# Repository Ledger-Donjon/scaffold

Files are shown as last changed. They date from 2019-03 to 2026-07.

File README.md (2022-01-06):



# Scaffold

When performing hardware security evaluation of integrated circuits and embedded
platforms, the first step is to setup the device to be able to automate tests,
retrieve results and trigger instruments to perform measurements or inject
faults. Scaffold is an electronic motherboard designed to quickly setup,
instrument and test cirtcuits. The board can be controlled through USB using a
Python3 API, enabling easy development of tests. All the project is
Open-Hardware and Open-Source.

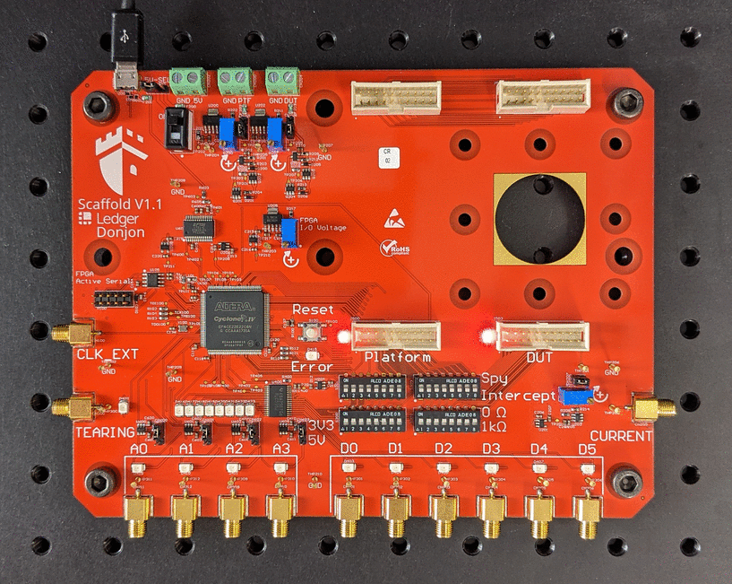
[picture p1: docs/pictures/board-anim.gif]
Scaffold board pictures


The FPGA architecture runs at 100 MHz and embeds many peripherals:

- 2 x UART,
- I2C (master),
- ISO7816 (master),
- SPI (master),
- Power supply controllers for each evaluation socket,
- 4 x Delay and pulse generators with 10 ns resolution
- 2 x chaining modules for advanced triggering
- Clock generator with glitching feature
- And more to come in the future!

The board also integrates an 11X analog amplifier with 200 MHz bandwidth for
power measurement. The on-board shunt resistor can be tuned from 0 to
100 Ohms.

Scaffold is able to operate from 1.5V to 3.3V devices: power supplies and I/O
bank voltage can be tuned thanks to adjustable voltage regulators. Scaffold can
be powered from USB or external power supplies.

Four special I/Os can generate 5V pulses, which are compatible with
*ALPhANOV PDM* laser sources (50 Ohm TTL).

## Getting the board

All the files required to fabricate the board are included in the repository.
If you do not wish to build it yourself, you can request for quotation by
sending a mail to scaffold@ledger.fr (only for Europe or USA shipping).

## Installation

Python3 library can be installed using pip:

    pip3 install donjon-scaffold

## Documentation

API documentation is available on [Read the Docs](https://donjonscaffold.readthedocs.io).

## Licensing

Scaffold is released under GNU Lesser General Public Licence version 3 (LGPLv3).
See COPYING and COPYING.LESSER for license details.

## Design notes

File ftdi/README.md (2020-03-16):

# FTDI EEPROM programming

Disconnect all USB-to-serial devices but the Scaffold board.

Install the package `ftdi_eeprom` and execute the `flash.sh` script as root to
program the EEPROM memory of the Scaffold FT232H device. This will configure
the vendor and description strings to respectively "Ledger" and "Scaffold".

Configuring the EEPROM is optional, but when programmed, the software is able
to recognize automatically which serial port corresponds to the Scaffold board.

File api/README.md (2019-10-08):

# scaffold board Python3 API

This is the Python3 API package for the Scaffold board.
See [Scaffold project on GitHub](https://github.com/Ledger-Donjon/scaffold).

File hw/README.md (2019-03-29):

## Authors

The hardware schematics and PCB have been designed by Julien Juan and
Guillaume Levant, at Ledger SAS.

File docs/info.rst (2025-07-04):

Product information
===================

Use and care
------------

Please handle your Scaffold board with care. The Scaffold board is not
waterproof. Make sure you use it indoor in a dry environment and keep away from
any liquids. This product is not a toy, make sure you keep it away from
children.

Changes or modifications to this product not expressly approved by Ledger could
void its compliance to test standards and negate the user's authority to operate
it.

If the product is used in a manner not specified by the manufacturer, the
protection provided by the equipment may be impaired.

Operating conditions
--------------------

For proper operation, the Scaffold board must be connected to a computer with
the USB2 cable. The product can be used with Linux, Windows and Mac. The board
API can be downloaded at https://github.com/Ledger-Donjon/scaffold.

+------------------------------------------+------------------------------------+
| USB supply voltage                       | 5 Vdc                              |
+------------------------------------------+------------------------------------+
| USB current rating                       | 1 A                                |
+------------------------------------------+------------------------------------+
| External supply voltage                  | 5 Vdc                              |
+------------------------------------------+------------------------------------+
| External supply current rating           | 1 A                                |
+------------------------------------------+------------------------------------+
| External platform supply maximum voltage | 5 Vdc                              |
+------------------------------------------+------------------------------------+
| External platform supply current rating  | 1 A                                |
+------------------------------------------+------------------------------------+
| External DUT supply maximum voltage      | 5 Vdc                              |
+------------------------------------------+------------------------------------+
| External DUT supply current rating       | 1 A                                |
+------------------------------------------+------------------------------------+
| For indoor use only                                                           |
+------------------------------------------+------------------------------------+
| Temperature range                        | 5°C to 40°C                        |
+------------------------------------------+------------------------------------+
| Maximum altitude                         | 2000 m                             |
+------------------------------------------+------------------------------------+
| Maximum relative humidity                | 80% up to 31°C,                    |
|                                          |                                    |
|                                          | Decreasing linearly to 50% at 40°C |
+------------------------------------------+------------------------------------+
| Expected pollution degree                | 2                                  |
+------------------------------------------+------------------------------------+

Three connectors allow using external power supplies instead of the 5 V USB
source. Power sources can be selected using the jumpers CN203, CN201 and CN206.
All the board can be powered using a single external power supply.
Independently, platform and DUT sockets can also be powered using external power
supplies.

External power supplies current must be limited to a current less than 5 A.
When using multiple power supplies, connect their ground signals together.

See :ref:`Using external power supplies <external_power_supplies>` for more information.

Manufacturer
------------

**Ledger**, 106 rue du Temple, 75003 Paris, France

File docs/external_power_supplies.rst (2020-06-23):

.. _external_power_supplies:

Using external power supplies
=============================

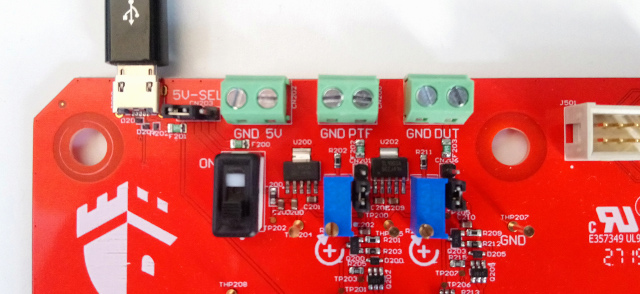
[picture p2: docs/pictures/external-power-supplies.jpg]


Three connectors allow using external power supplies instead of the 5 V USB
source.

- First green connector "GND 5V" allows connecting a 5 V - 1 A power source
  for powering all the board. The jumper "5V-SEL" on the left must be set to the
  right to disconnect the USB power source and connect the external power supply
  instead.

- Second green connector "GND PTF" allows connecting a 5 V - 1 A power source
  for powering the platform socket. The jumper below must be set to the top to
  disconnect the board power source and connect the external power supply
  instead.

- Third green connector "GND DUT" allows connecting a 5 V - 1 A power source
  for powering the Device Under Test platform socket. The jumper below must be
  set to the top to disconnect the board power source and connect the external
  power supply instead.

External power supplies current must be limited to a current less than 5 A.
When using multiple power supplies, connect their ground signals together.

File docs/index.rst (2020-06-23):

.. scaffold documentation master file, created by
   sphinx-quickstart on Fri Jul 13 13:31:07 2018.
   You can adapt this file completely to your liking, but it should at least
   contain the root `toctree` directive.

Welcome to scaffold's documentation!
====================================



.. toctree::
   :maxdepth: 2
   :caption: Contents:

   Getting started <getting_started.rst>
   Product information <info.rst>
   Platform and DUT sockets <sockets.rst>
   Using external power supplies <external_power_supplies.rst>
   Kits <kits.rst>
   Scaffold peripherals <peripherals.rst>
   Python API reference <api.rst>
   Architecture <architecture.rst>
   Building and flashing the FPGA bitstream <building_bitstream.rst>

Indices and tables
==================

* :ref:`genindex`
* :ref:`modindex`
* :ref:`search`

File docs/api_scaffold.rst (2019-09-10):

Main Scaffold API
=================

This page documents the main classes and methods of the Scaffold Python API.

Manipulating the attributes of the different modules of a :class:`Scaffold`
instance will read or write in the FPGA registers. Some registers may be cached
by the Python API, so reading them does not require any communication with the
board and thus can be fast.

.. automodule:: scaffold

.. autoclass:: Scaffold
    :members: __init__

.. autoclass:: Signal
    :special-members: __init__, __str__, __lshift__
    :members:

.. autoclass:: IO
    :members:

.. autoclass:: IOMode
    :members:
    :undoc-members:

.. autoclass:: Pull
    :members:
    :undoc-members:

.. autoclass:: UARTParity
    :members:
    :undoc-members:

.. autoclass:: UART
    :members:

.. autoclass:: ISO7816
    :members:

.. autoclass:: I2C
    :members:

.. autoclass:: SPI
    :members:

.. autoclass:: PulseGenerator
    :members:

.. autoclass:: Clock
    :members:

.. autoclass:: Chain
    :members:

.. autoclass:: LEDs
    :members:

.. autoclass:: Power
    :members:

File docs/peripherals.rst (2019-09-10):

Scaffold peripherals
====================

The FPGA system has many modules wrapping communication peripherals or utility
hardware. Each module exposes registers which can be read or written. Each
register has a unique address.

Every module has input and output signals. Thoose signals are illustrated in
each peripheral documentation like the following example:

.. modbox::
    :inputs: input_a, input_b
    :outputs: output_a, output_b, output_c*

Input and output signals can be routed to Scaffold I/Os. Some special output
signals have a feedback path and can be routed to other peripheral inputs.
Thoose are usually trigger signals and are represented with an extra arrow like
the signal `output_c` in the example above.

.. toctree::
  :caption: Contents:

   I/Os <ios.rst>
   UART <uart_module.rst>
   Power <power_module.rst>
   LEDs <leds_module.rst>
   ISO7816 <iso7816_module.rst>
   I2C <i2c_module.rst>
   SPI <spi_module.rst>
   Pulse generator <pulse_generator_module.rst>
   Clock generator <clock_module.rst>
   Chain triggers <chain_module.rst>
   Version <version_module.rst>

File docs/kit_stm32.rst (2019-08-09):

STM32F2 kits
============

STM32 kits allows communicating with the embedded ST bootloader of STM32F205 and
STM32F427 devices. It is possible to write the Flash memory to load code, and
then execute it after reset.

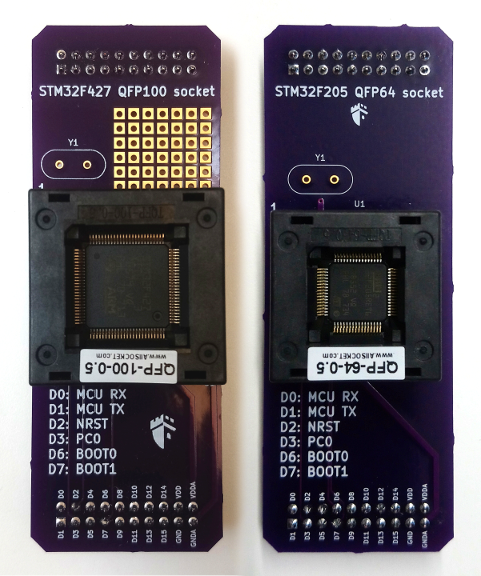
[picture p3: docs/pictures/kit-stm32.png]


Those QFP64 and QFP100 may suit other STM32 devices. Some breadboard space
allows customizing the daughterboard for special needs, such as clock or voltage
glitch electronics.

Python API example
------------------

The class :class:`scaffold.stm32.STM32` of the Python API provides methods to
communicate with the circuit and setup tests very quickly.

.. code-block:: python

    from scaffold import Scaffold
    from scaffold.stm32 import STM32

    stm = STM32(Scaffold('/dev/ttyUSB0'))
    # Load some code into Flash memory
    stm.startup_bootloader()
    stm.extended_erase()
    stm.write_memory(0x08000000, open('program.bin', 'rb').read())
    # Run the program
    stm.startup_flash()

Example script
--------------

An example file in `examples/stm32.py` can be used to load and execute code
onto a STM32F2 device.

.. code-block:: console

    $ python3 stm32.py -d /dev/ttyUSB0 --load program.bin --run
    Communication initiated
    Product ID: 0x0411
    Possible device match: stm32f2xxxx
    Get: 310001021121314463738292
    Bootloader version: 3.1
    Option bytes: ffaa0055ffaa0055ffff0000ffff0000
    RDP: no protection
    Erasing Flash memory...
    Programming...
    Verifying...
    Flash memory written successfully!
    Rebooting from Flash memory...

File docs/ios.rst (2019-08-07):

I/Os
====

The Scaffold Python API allows controlling and reading the I/Os of the board.
This can be useful, for instance, to control the reset signal of a device under
test. The following example shows how easy this can be done.

.. code-block:: python

    # Toggle D0 every second.
    for i in range(10):
        scaffold.d0 << 0
        time.sleep(1)
        scaffold.d0 << 1
        time.sleep(1)

    # Put D0 in high impedance state
    scaffold.d0 << None
    time.sleep(1)

    # Connect the output to the internal UART peripheral TX signal, and send a
    # message !
    scaffold.d0 << scaffold.uart0.tx
    scaffold.uart0.send('Hello world!')

It is also possible to read the current electrical state of an input of the
board:

.. code-block:: python

    if scaffold.d0.value == 1:
        print('Input is high!')

Finally, you can watch for events on an input. The event will be asserted if a 1
is detected. This works for short pulses (> 10 ns).

.. code-block:: python

    # Reset event flag
    scaffold.d0.event = 0
    # Wait some time
    time.sleep(1)
    # Lookup event register to know if a pulse has been received
    if scaffold.d0.event == 1:
        print('Event detected!')
        scaffold.d0.clear_event()

.. warning::
    I/Os internals have been refactored in 0.3. Registers are not the same as in
    0.2. Current API supports both 0.2 and 0.3 versions.

Programmable pull-resistors
---------------------------

Scaffold hardware version 1.1 comes with programmable pull resistors for D0, D1
and D2. This can replace pull-up resistors which were necessary for
bidirectionnal buses like the I/O signal of the ISO7816 interface. The pull
resistor can be configured using the Python API, as shown in the following
example:

.. code-block:: python

    scaffold.d0.pull = Pull.UP
    scaffold.d1.pull = Pull.DOWN
    scaffold.d2.pull = None  # Pull.NONE also accepted

Pull resistor value is 10 kOhm. When pull resistor is disabled, there is still
a weak pull-up resistor from the FPGA I/O itself.

Internal registers
------------------

+----+-------------------+
| a0 | 0xe000            |
+----+-------------------+
| a1 | 0xe010            |
+----+-------------------+
| a2 | 0xe020            |
+----+-------------------+
| a3 | 0xe030            |
+----+-------------------+
| dn | 0xe060 + 0x10 * n |
+----+-------------------+

+---------------+--------+-----+
| base + 0x0000 | value  | R/W |
+---------------+--------+-----+
| base + 0x0001 | config | W   |
+---------------+--------+-----+

value register
--------------

+---+---+---+---+---+---+-------+-------+
| 7 | 6 | 5 | 4 | 3 | 2 | 1     | 0     |
+---+---+---+---+---+---+-------+-------+
| *reserved*            | event | value |
+-----------------------+-------+-------+

value
  Reading this bit will return current logical state on the I/O.
  Setting this bit has no effect.
event
  This bit is set to 1 when the I/O logical state changes. It can be reset by
  writing 0 to it.

config register
---------------

+---+---+---+---+---+---+---+---+
| 7 | 6 | 5 | 4 | 3 | 2 | 1 | 0 |
+---+---+---+---+---+---+---+---+
| *reserved*    | pull  | mode  |
+---------------+-------+-------+

This register allows customizing the output mode of an I/O.

+------+----------------------------------------------------------------------+
| mode | Description                                                          |
+------+----------------------------------------------------------------------+
| 0    | **Auto**                                                             |
|      |                                                                      |
|      | The pin is driven by the routed peripheral.                          |
+------+----------------------------------------------------------------------+
| 1    | **Open-drain**                                                       |
|      |                                                                      |
|      | The pin is driven by the routed peripheral, but always acts as an    |
|      | open-collector.                                                      |
+------+----------------------------------------------------------------------+
| 2    | **Push-only**                                                        |
|      |                                                                      |
|      | The pin is driven by the routed peripheral, but is active only when  |
|      | a one is outputed.                                                   |
+------+----------------------------------------------------------------------+

If the I/O supports it, the pull resistor configuration can be configured. For
Scaffold hardware v1, no I/O supports this option. For Scaffold hardware v1.1,
the D0, D1 and D2 I/Os supports this option.

+------+--------------------+
| pull | Description        |
+------+--------------------+
| 0    | No pull resistor.  |
+------+--------------------+
| 1    | Pull-down resistor |
+------+--------------------+
| 2    | No pull resistor.  |
+------+--------------------+
| 3    | Pull-up resistor   |
+------+--------------------+

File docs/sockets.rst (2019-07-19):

Platform and DUT sockets
========================

The following figure is a simplified drawing for the Scaffold v1.1 socket
footprints. It can be used to design custom daughter-boards.

Female HE10 connectors can be used on the daughter-boards. All holes are aligned
on a 2.54 mm (100 mil) grid, which is compatible with most of the prototyping
breadboards for very cheap daughter-board making.



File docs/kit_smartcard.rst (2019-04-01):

Smartcard kit
=============

This kit allows communicating with any smartcard using 7816 protocol.

The class :class:`scaffold.iso7816.Smartcard` of the Python API provides
methods to communicate with an ISO7816 Smartcard and setup tests very quickly.
Currently, only T=0 protocol is supported by the API and it has not been tested
extensively yet.

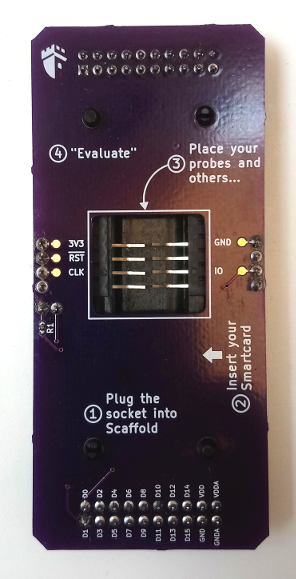
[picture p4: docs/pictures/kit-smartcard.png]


Pinout
------

+----+---------------------------------------------------------------------+
| D0 | I/O. This signal is pulled up with a resistor on the daughter board |
+----+---------------------------------------------------------------------+
| D1 | nRST                                                                |
+----+---------------------------------------------------------------------+
| D2 | CLK                                                                 |
+----+---------------------------------------------------------------------+
| D3 | Socket card presence contactor                                      |
+----+---------------------------------------------------------------------+

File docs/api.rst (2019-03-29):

Python API
==========
.. toctree::
  :caption: Contents:

  Scaffold <api_scaffold.rst>
  STM32 <api_stm32.rst>
  ISO7816 <api_iso7816.rst>

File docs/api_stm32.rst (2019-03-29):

STM32 API
=========

This API is for STM32 experimental daughter boards.

.. automodule:: scaffold.stm32

.. autoclass:: STM32
    :special-members: __init__
    :members:

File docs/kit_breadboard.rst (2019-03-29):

Breadboard kit
==============

The Scaffold breadboard provides solderable test points for all the DUT socket
pins. It can be used to mount a setup with any target.

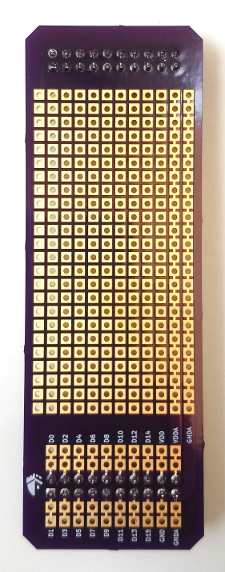
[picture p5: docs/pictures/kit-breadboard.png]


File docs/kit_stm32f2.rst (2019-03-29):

STM32F2 QFP64 kit
=================

This kit allows communicating with the embedded ST bootloader of STM32F2
devices. It is possible to write the Flash memory to load code, and then
execute it after reset.

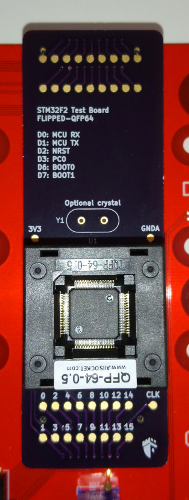
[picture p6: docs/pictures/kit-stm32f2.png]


The socket FLIPPED-QPF64 can be used to mount a STM32F2 device on its backside.
All pins of the package must be returned before inserting the device in the
socket. Pin 1 of the target device is as shown in the figure above. Make sure
the device is correctly inserted and all the needles of the socket touch their
corresponding PIN.

Python API example
------------------

The class :class:`scaffold.stm32.STM32` of the Python API provides methods to
communicate with the circuit and setup tests very quickly.

.. code-block:: python

    from scaffold import Scaffold
    from scaffold.stm32 import STM32

    stm = STM32(Scaffold('/dev/ttyUSB0'))
    # Load some code into Flash memory
    stm.startup_bootloader()
    stm.extended_erase()
    stm.write_memory(0x08000000, open('program.bin', 'rb').read())
    # Run the program
    stm.startup_flash()

Example script
--------------

An example file in `examples/stm32.py` can be used to load and execute code
onto a STM32F2 device.

.. code-block:: console

    $ python3 stm32.py -d /dev/ttyUSB0 --load program.bin --run
    Communication initiated
    Product ID: 0x0411
    Possible device match: stm32f2xxxx
    Get: 310001021121314463738292
    Bootloader version: 3.1
    Option bytes: ffaa0055ffaa0055ffff0000ffff0000
    RDP: no protection
    Erasing Flash memory...
    Programming...
    Verifying...
    Flash memory written successfully!
    Rebooting from Flash memory...

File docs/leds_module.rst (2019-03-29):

LEDs module
===========

The LEDs module allows controlling the LEDs of the board.

Python API example
------------------

.. code-block:: python

    # Adjust LEDs brightness
    # 0 is minimum
    # 1 is maximum
    scaffold.leds.brightness = 0.5

    # Toggle a LED every second
    scaffold.leds.d0.mode = LEDMode.VALUE
    for i in range(10):
        time.sleep(1)
        scaffold.d0 << 1
        time.sleep(1)
        scaffold.d0 << 0

    # Now flash the LED every second
    scaffold.leds.d0.mode = LEDMode.EVENT
    for i in range(10):
        time.sleep(1)
        scaffold.d0 << 1
        time.sleep(1)
        scaffold.d0 << 0

LEDs mode
---------

A/B/C/D LEDs can be lit according to two different modes:

- Event mode: the LED will flash when an rising or falling edge occurs on the
  monitored signal. This is the default mode. This mode allows seeing activity
  on the LED even when very short pulses happen.
- Value mode: the LED is ON when the monitored signal is high. When using this
  mode, a user may not be able to catch very short pulses. This mode is more
  appropriate for watching slow signals.

Registers
---------

+--------+------------+---+
| 0x0200 | control    | W |
+--------+------------+---+
| 0x0201 | brightness | W |
+--------+------------+---+
| 0x0202 | leds_0     | W |
+--------+------------+---+
| 0x0203 | leds_1     | W |
+--------+------------+---+
| 0x0204 | leds_2     | W |
+--------+------------+---+
| 0x0205 | mode       | W |
+--------+------------+---+

control register
^^^^^^^^^^^^^^^^

+---+---+---+---+---+---+----------+---------+
| 7 | 6 | 5 | 4 | 3 | 2 | 1        | 0       |
+---+---+---+---+---+---+----------+---------+
| *reserved*            | override | disable |
+-----------------------+----------+---------+

disable
  Write 1 to disable TLC5927 drivers output. Default is 0 (enabled).
override
  Sets the LEDs of the board to the values defined in led_n registers.

brightness registers
^^^^^^^^^^^^^^^^^^^^

+------------+---+---+---+---+---+---+---+
| 7          | 6 | 5 | 4 | 3 | 2 | 1 | 0 |
+------------+---+---+---+---+---+---+---+
| *reserved* | brightness                |
+------------+---------------------------+

brightness
  7-bits word which controls the brightness of the LEDs. See TLC5952 datasheet
  for more details.

leds_n registers
^^^^^^^^^^^^^^^^

*leds_n* registers define the state of the LEDs of the board when override bit
is set. Set a bit to 1 to turn the corresponding LED on, 0 to turn it off. Value
on reset is 0x00.

mode register
^^^^^^^^^^^^^

+----+----+----+----+----+----+----+----+----+----+----+----+----+----+----+----+----+----+---+---+---+---+---+---+
| 23 | 22 | 21 | 20 | 19 | 18 | 17 | 16 | 15 | 14 | 13 | 12 | 11 | 10 | 9  | 8  | 7  | 6  | 5 | 4 | 3 | 2 | 1 | 0 |
+----+----+----+----+----+----+----+----+----+----+----+----+----+----+----+----+----+----+---+---+---+---+---+---+
| *reserved*                  | d5 | d4 | d3 | d2 | d1 | d0 | c1 | c0 | b1 | b0 | a1 | a0 | *reserved*            |
+-----------------------------+----+----+----+----+----+----+----+----+----+----+----+----+-----------------------+

mode register is a 24-bit register. Write three times to update all the bits of
this register.

Each bit of this register sets the lighting mode of a LED. When bit is 0, the
corresponding LED will blink on a falling or rising edge of the monitored
signal. When the bit is 1, the LED will be lit as long as the monitored
signal is high. Default mode is 0 (event mode) for all LEDs.

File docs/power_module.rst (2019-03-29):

Power module
============

The power module controls two power supplies: the "platform" socket power
supply and the "dut" socket power supply. Each power supply can be turned
on and off. 

A positive input pulse on the "tearing" input of the board (SMA connector on
the left side) will automatically power-off both power supplies.

Python API example
------------------

.. code-block:: python

    # Turn DUT on
    scaffold.power.dut = 1 # True is also valid
    # Check current power supply status
    # (it may be off due to external tearing)
    if scaffold.power.dut: # Will return 0 or 1
        print('DUT is still ON')
    # Turn DUT off
    scaffold.power.dut = 0 # False is also valid

The following example controls both power supplies at the same time.

.. code-block:: python

    # Turn on all power supplies
    scaffold.power.all = 0b11 
    # Check current power status of both power supplies
    if (scaffold.power.all == 0b11):
        print('Both power supplies are ON')
    # Turn off all power supplies
    scaffold.power.all = 0b00

It is also possible to output the power enable signal to one of the IOs, for
triggering or monitoring:

.. code-block:: python

    scaffold.d0 << scaffold.power.dut_trigger

For more API documentation, see :class:`scaffold.Power`

Internal registers
------------------

+---------+--------+
| control | 0x0600 |
+---------+--------+

control register
^^^^^^^^^^^^^^^^

+---+---+---+---+---+---+----------+-----+
| 7 | 6 | 5 | 4 | 3 | 2 | 1        | 0   |
+---+---+---+---+---+---+----------+-----+
| *reserved*            | platform | dut |
+-----------------------+----------+-----+

dut
  Write 1 to enable the DUT socket power supply. Write 0 to disable. This bit
  is cleared when the tearing input is high.
platform
  Write 1 to enable the platform socket power supply. Write 0 to disable. This
  bit is cleared when the tearing input is high.

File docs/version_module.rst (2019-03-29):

Version module
==============

This module helps the software identifying the board. When
:class:`scaffold.Scaffold` connects to the board, the version string is
automatically queried and cached in the version attribute.

Python API example
------------------

.. code-block:: python

    # Read cached version string
    # Shall return something like 'scaffold-1.0'
    print(scaffold.version)

Internal registers
------------------

+--------+------+---+
| 0x0100 | data | R |
+--------+------+---+

data register
^^^^^^^^^^^^^

Reading multiple times this register will return the version string of the
board. A null character indicates the beginning (and end) of the version
string. Latest version string is "scaffold-1.0".

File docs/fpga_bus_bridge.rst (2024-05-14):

FPGA bus bridge
===============

The bus bridge allows reading and writing bytes on the internal FPGA bus using
commands sent in serial. This bridge is implemented in VHDL using a Finite State
Machine. The state machine manages the commands parsing and execution.

The state machine has a lot of states and is a bit complex. However, the parsing
and execution of a command is faster than the time required to receive an
incoming new command - making it hard to saturate the commands queue. The only
cases a command queue can be overflowed is when using polling commands - in such
cases the application may wait for the response before sending further commands.

Overflowing the commands queue will usually lead to entering the
error state as bytes will be discarded, resulting in data bytes being
interpreted as invalid command codes. When in error state, the error LED on the
board is lit. The only way to recover from the error state is pressing the reset
button.

State machine
*************

The following graph is the bus bridge finite state machine implemented in the
FPGA. This document is an help for understanding FPGA internals.

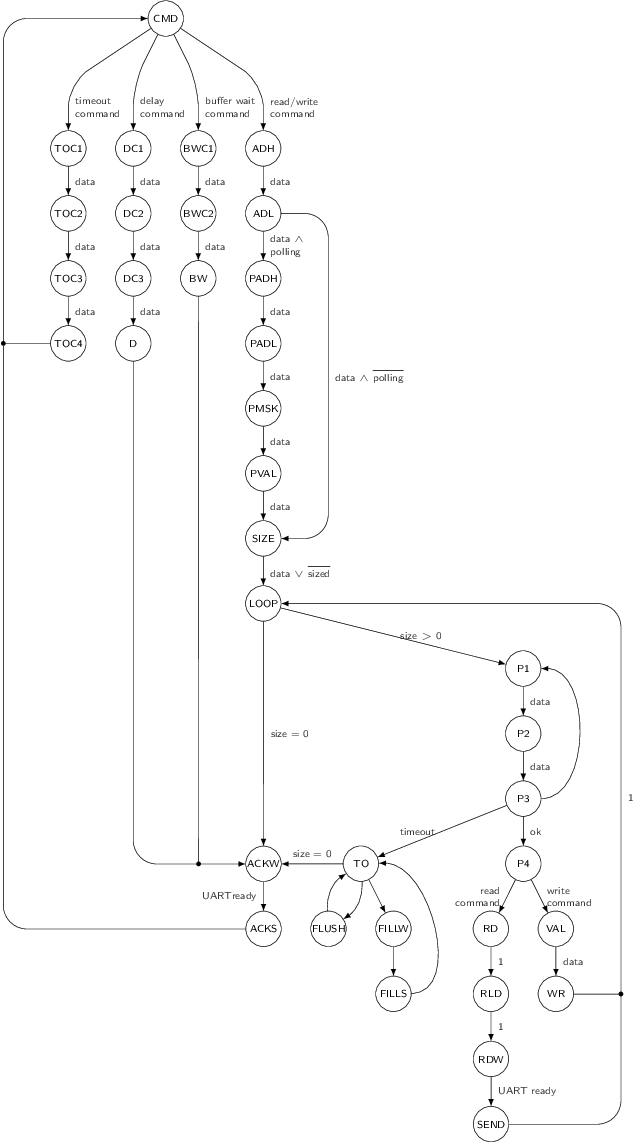
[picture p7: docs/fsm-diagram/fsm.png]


Details on states:

- ``CMD``: Idle state, awaiting for command byte.
- ``ADH``: Awaiting for read/write address high nibble.
- ``ADL``: Awaiting for read/write address low nibble.
- ``PADH``: Awaiting for polling address high nibble.
- ``PADL``: Awaiting for polling address low nibble.
- ``PMSK``: Awaiting for polling mask.
- ``PVAL``: Awaiting for polling value.
- ``SIZE``: Read/write size fetch. If the command does not require size
  parameter, use value 1 by default. Otherwise, wait and store next byte
  received on UART.
- ``LOOP``: Preload polling address on the bus for P1 and P2 states. Return to
  initial state if all bytes have been read or written.
- ``ACKW``: Wait for UART to be ready to transmit an acknoledge byte. This also
  acts as a delay cycle required for data bus to be available (due to
  pipelining).
- ``ACKS``: Send result byte on UART (command acknowledge or register value).
- ``P1``: First polling state. Assert bus read signal. Due to pipelining, the
  data read from the bus is available to the rest of the logic at ``P2``.
- ``P2``: Second polling state. Used for pipelining (registers the data read
  from the bus).
- ``P3``: Polling test. If polling value matches, leave polling by going to
  ``P4``. Otherwise, return to ``P1`` for a new polling read cycle.
- ``P4``: End of polling. Load register address on the bus.
- ``VAL``: Read from UART the byte to be written in register.
- ``WR``: Register write cycle.
- ``RD``: Register read cycle.
- ``RLD``: Register load cycle, waits for the read data to be available on the
  bus.
- ``RDW``: Wait for UART to be ready to transmit the read byte.
- ``RDS``: Send the read byte via UART.
- ``TO``: Timeout state. Loops until all unprocessed bytes have been discarded
  (write operation) or returned as zeros (read operation).
- ``FLUSH``: Cycle used to discard a byte from the input FIFO during a write
  operation which has timed out.
- ``FILLW``: Wait for UART to be ready.
- ``FILLS``: Transmit a filling byte to replace unread bytes.
- ``TOC1``: Awaiting for timeout configuration first byte.
- ``TOC2``: Awaiting for timeout configuration second byte.
- ``TOC3``: Awaiting for timeout configuration third byte.
- ``TOC4``: Awaiting for timeout configuration fourth byte.
- ``BWC1``: Awaiting for buffer wait configuration first byte.
- ``BWC2``: Awaiting for buffer wait configuration second byte.
- ``BW``: Awaiting for command buffer to be complete.
- ``DC1``: Awaiting for delay first byte.
- ``DC2``: Awaiting for delay second byte.
- ``DC3``: Awaiting for delay third byte.
- ``D``: Delay operation. Exits when the delay counter reaches 0.

Details on transition conditions:

- ``1``: Unconditionally pass to the next state at the next clock cycle.
- ``data``: True when the UART FIFO has a byte available.
- ``size``: Number of remaining bytes to be read or written.
- ``ready``: True when the UART of the bus bridge is ready to transmit a byte.
- ``read_command``: True when the fetched command byte corresponds to a bus read
  cycle command.
- ``write_command``: True when the fetched command byte corresponds to a bus
  write cycle command.
- ``buf_wait_command``: True when the fetched command byte corresponds to a bus
  buffer wait command.
- ``delay_command``: True when the fetched command byte corresponds to a bus
  delay command.

Polling timeout configuration
*****************************

A special command bit allows reconfiguring the polling timeout delay. The delay
parameter is stored in an internal 32 bits register and encodes a number of
clock cycles to wait during polling state (1 unit equals to 3 clock cycles).
When this register is set to 0, the timeout is disabled. Note that disabling
the timeout is not recommended since the FSM may stuck in a polling operation
forever or until general reset.

The maximum possible timeout duration is approximately 128 seconds.

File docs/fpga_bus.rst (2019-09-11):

FPGA bus
========

The internal global bus connects all the peripherals together. This bus is
controlled by the serial bridge which is connected to the host computer with
the USB link. The bus can perform only two simple operations:

- Read a byte from a register,
- Write a byte to a register.

The bus works using many signals:

- 16-bits address: bus_address,
- Write assertion signal: bus_write
- 8-bits write data: bus_write_data,
- Read assertion signal: bus_read
- 8-bits read data: bus_read_data

Using different data wires for read and write operations makes conflicts
between modules impossible. Also, some FPGA devices may not allow internal
bidirectional wires.

All the signals of the bus are synchronized to the system clock, on rising
edges.

Register read cycle
-------------------

.. wavedrom::

    { "signal": [
        {"name": "clock", "wave": "P...."},
        {"name": "bus_address", "wave": "x=x..", "data": ["address"]},
        {"name": "bus_read", "wave": "010.."},
        {"name": "bus_read_data", "wave": "x.=x.", "data": ["data"]},
        {"name": "bus_write", "wave": "0...."},
        {"name": "bus_write_data", "wave": "x...."}
        ],
      "config": { "hscale": 1.5, "vscale": 1.5 }
    }

|

Peripherals connected to the bus must present valid data one clock cycle after
the `bus_read` signal is asserted. This allow using FIFO blocks with
*read-ahead* option disabled, which is more performant.

Register write cycle
--------------------
    
.. wavedrom::    
    
    { "signal": [
        {"name": "clock", "wave": "P...."},
        {"name": "bus_address", "wave": "x=x..", "data": ["address"]},
        {"name": "bus_read", "wave": "0...."},
        {"name": "bus_read_data", "wave": "x...."},
        {"name": "bus_write", "wave": "010.."},
        {"name": "bus_write_data", "wave": "x=x..", "data": ["data"]}
        ],
      "config": { "hscale": 1.5, "vscale": 1.5 }
    }

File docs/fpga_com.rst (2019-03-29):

Communication protocol
======================

General architecture
--------------------

The FPGA has many embedded peripherals. Each peripheral has registers which can
be read/written to receive/send data and perform actions. Each register is
assigned a unique 16-bits address and is connected to the system data bus.

A bridge controller, inside the FPGA, controls the read and write operations on
the system data bus. This controller can be driven by a host computer using the
USB link, allowing the host computer to manipulate the registers connected to
the system data bus.

Protocol
--------

When connected to a host computer using a USB cable, the board is recognized as
a USB-to-Serial device from FTDI manufacturer. Baudrate is 2 Mbits/s, with one
stop bit and no parity check.

A very simple protocol is defined to perform read and write operations through
the serial device. To perform an operation, the following data must be sent to
Scaffold:

+----------------------+---------+----------------------+
| Command              | 1 byte  | Mandatory            |
+----------------------+---------+----------------------+
| Address              | 2 bytes | Mandatory            |
+----------------------+---------+----------------------+
| Polling address      | 2 bytes | When polling enabled |
+----------------------+---------+----------------------+
| Polling mask         | 1 byte  | When polling enabled |
+----------------------+---------+----------------------+
| Polling value        | 1 byte  | When polling enabled |
+----------------------+---------+----------------------+
| Size                 | 1 byte  | When size enabled    |
+----------------------+---------+----------------------+
| Data                 | N bytes | For write commands   |
+----------------------+---------+----------------------+

Bit 0 of command byte indicates if this is a read (0) or write (1) command.
Bit 1 indicates if size parameter is present (1 to enable size).
Bit 2 indicates if polling is requested for this command (1 to enable polling).
All other bits must be set to zero, otherwise the command is considered invalid
and Scaffold will enter error mode.

For write and read commands, a response is transmitted by the Scaffold board.
This response starts by the data bytes (for register read commands) and
terminates with a status byte. The status byte shall be equal to the size of the
processed data. If a command times out during polling, the returned status byte
will be lower than the size of the data.

Register polling
----------------

Read or write operations on registers can be conditioned to a given register
expected state. When polling is enabled, each read or write operation is
performed when the monitored register reaches a given value for some chosen
bits. Polling is enabled when bit 2 of command byte is 1. Read or write
operation is performed when ``(Register and Mask) = (Value and Mask)``.

Polling can be used for flow control when using a peripheral to process multiple
bytes. For instance, when using a SPI peripheral, polling can be used to wait
for incoming bytes.

The polled register can be different from the read or written register (two
different addresses can be passed in the command parameters: address and polling
address).

Polling timeout
---------------

Optionally, a timeout can be configured for polling operations. This is
particularly useful if receiving bytes from a peripheral is not guaranteed. When
the polling times out in a read operation, the remaining expected bytes are sent
by the board as zero. When the polling times out in a write operation, the
remaining bytes sent to the board are discarded by the bus bridge. The returned
acknowledge byte indicates the number of successfully processed bytes and will
be lower than the requested size in the command.

The timeout delay can be configured with a special command:

+----------------------+---------+----------------------+
| Command 0x08         | 1 byte  | Mandatory            |
+----------------------+---------+----------------------+
| Polling delay value  | 4 bytes | MSB first            |
+----------------------+---------+----------------------+

No response is expected after this command. The new delay value will be applied
for all the following commands. If the delay is set to zero, then the timeout is
disabled (which is the default).

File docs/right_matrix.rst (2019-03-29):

Output module
=============

The available I/Os of the scaffold board can be internally connected to any
module output. The "right matrix" controls which module output signals are
connected to which I/Os. Each I/O has a register storing its multiplexer
selecting the source signal.

Multiplexers selection table
----------------------------

+-------+-------------------------+
| Index | Signal name             |
+=======+=========================+
| 0     | z                       |
+-------+-------------------------+
| 1     | 0                       |
+-------+-------------------------+
| 2     | 1                       |
+-------+-------------------------+
| 3     | /power/dut_trigger      |
+-------+-------------------------+
| 4     | /power/platform_trigger |
+-------+-------------------------+
| 5     | /uart0/tx               |
+-------+-------------------------+
| 6     | /uart0/trigger          |
+-------+-------------------------+
| 7     | /uart1/tx               |
+-------+-------------------------+
| 8     | /uart1/trigger          |
+-------+-------------------------+
| 9     | /iso7816/io_out         |
+-------+-------------------------+
| 10    | /iso7816/clk            |
+-------+-------------------------+
| 11    | /iso7816/trigger        |
+-------+-------------------------+
| 12    | /pgen0/out              |
+-------+-------------------------+
| 13    | /pgen1/out              |
+-------+-------------------------+
| 14    | /pgen2/out              |
+-------+-------------------------+
| 15    | /pgen3/out              |
+-------+-------------------------+

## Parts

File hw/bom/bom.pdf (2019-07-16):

Quantity | Designator | Description | Manufacturer | Manufacturer PN | Manufacturer1 | Manufacturer1 PN | Manufacturer2 | Manufacturer2 PN
13 | C100, C101, C137, C200, C201, C202, C203, C204, C208, C209, C210, C217, C218 | Capacitor 0603 - 10uF - 16V - X5R - 20% | Murata | GRM188R61C106MA73D | TDK | C1608X5R1C106M080AB | Taiyo Yuden | EMK107BBJ106MA-T
51 | C102, C103, C104, C105, C106, C107, C108, C109, C110, C111, C112, C113, C114, C115, C116, C117, C118, C119, C120, C121, C122, C123, C124, C125, C126, C127, C128, C129, C130, C131, C132, C133, C134, C135, C136, C151, C153, C154, C205, C401, C600, C601, C602, C603, C605, C606, C607, C608, C609, C610, C611 Capacitor 0603 - 100nF - 16V - X7R - 10% | | Wurth | 885012206046 | Yageo | CC0603KRX7R7BB104 | Multicomp | MCCA000159
4 | C143, C144, C145, C146 | Capacitor 0603 - 10pF - 100V - COG - 5% | TDK | C1608C0G2A100D | Murata | GCM1885C2A100J | Samsung | CL10C100JC81PB
11 | C206, C207, C211, C212, C213, C214, C215, C216, C219, C220, C400 | Capacitor 0603 - 1uF - 16V - X7R - 10% | Kemet | C0603C105K4RACTU | Murata | GCM188R71C105K | Wurth | 885012206052
1 | C604 | Capacitor 0603 - 4.7uF - 16V - X5R - 10% | Murata | GRM188R61C475KE11 | TDK | C1608X5R1C475K080AC
13 | CN100, CN205, CN300, CN301, CN302, CN303, CN304, CN305, CN306, CN309, CN310, CN311, CN312 | Connector - SMA - Female - Horizontal - Mid Mount - Samtec - SMA–J–P–H–ST–EM3 | Samtec | SMA–J–P–H–ST–EM3
3 | CN200, CN202, CN204 | Connector - Wire to Board Terminal Block - 2-Positions - Wurth - 691213710002 | Wurth | 691213710002
7 | CN201, CN203, CN206, CN600, CN601, CN602, CN603 | Connector - Header - 3-Pin - single row - Male - Molex_90120-0123 | Molex | 90120-0123
1 | CN207 | Connector - Header - 2-Pin - single row - Male - Molex | Molex | 90120-0122
8 | D100, D101, D102, D103, D200, D201, D205, D206 | BAT60J | STMicroelectronics | BAT60J
3 | D202, D203, D204 | Diode - ESD -15kV -10GHz - ESDAXLC6-1BT2 | STMicroelectronics | ESDAXLC6-1BT2
2 | D400, D401 | Opto - DEL - RG 630/572nm 250/60 mcd - 20mA | Wurth | 150141RV73100
19 | D402, D403, D404, D405, D406, D407, D408, D409, D410, D411, D412, D416, D417, D418, D419, D420, D421, D422, D423 | Opto - DEL - Yellow 590nm - 2mA -30 mcd | Kingbright | AA3528LSYCKT/J3
1 | D415 | Opto - DEL - Red 625nm - 2mA -120 mcd | Kingbright | AA3528LSECKT/J3
4 | F200, F201, F202, F203 | Fuse 0805 - PTC Resettable - 1A - 0.5A - 6VDC - 0.9Ohms | Bel Fuse | 0ZCK0050FF2E | Bourns | MF-PSMF050X-2 | Littelfuse | 0805L050WR
1 | J200 | Connector - USB - Micro B - Wurth | Wurth | 629-105-150-521
4 | J500, J501, J502, J503 | Connector - Header - 20 Pins - Dual row - Shrouded - Male | Samtec | HTSS-110-01-G-D
3 | L100, L101, L200 | Ferrite - Bead - 0603 BLM18 | MURATA | BLM18KG101TN1D
1 | P100 | Connector - Header - 10 Pins - Dual row - Male | Samtec | TSW-105-07-G-D
2 | Q200, Q203 | Switch - PMOS 30V - STR2P3LLH6 - SOT23 | STMicroelectronics | STR2P3LLH6 | ON Semiconductor CPH3355-TL-W | | MCC | SI2307-TP
4 | Q201, Q202, Q204, Q205 | Switch - NMOS 30V - STT6N3LLH6 - SOT23-6 | STMicroelectronics | STT6N3LLH6
1 | R100 | Resistor 0603 - 47KOhm - 1/10W - 1% | YAGEO | RC0603FR-0747KL
20 | R101, R102, R103, R104, R105, R107, R108, R110, R111, R112, R301, R338, R339, R348, R349, R600, R601, R602, R604, R605 | Resistor 0603 - 10KOhm - 1/10W - 1% | Yageo | RC0603FR-0710KL | Panasonic | ERJ3EKF1002 | KOA Speer | RK73H1JHT..1002F
3 | R200, R207, R216 | Potentiometer - 50 kOhms - 10% - 0.5W - Bourns - 3296W-1-503RLF | Bourns Electronics | 3296W-1-503RLF
2 | R201, R209 | Resistor 0603 - 470Ohm - 1/10W - 1% | Yageo | RC0603FR-07470RP | Panasonic | ERJ3EKF4700 | KOA Speer | RK73H1JTTD4700F
2 | R202, R211 | Resistor 0603 - 15KOhm - 1/10W - 1% | Yageo | RC0603FR-1015KL | Panasonic | ERJ3EKF1502 | KOA Speer | RK73H1JHT..1502F
4 | R203, R204, R212, R213 | Resistor 0603 - 2Ohm - 1/10W - 1% | Vishay | CRCW06032R00FKEA
19 | R205, R214, R215, R304, R306, R308, R312, R316, R318, R320, R322, R326, R330, R332, R334, R340, R342, R346, R350 | Resistor 0603 - 1KOhm - 1/10W - 1% | Yageo | RC0603FR-071KL
1 | R206 | Resistor 0603 - 50Ohm - 1/10W - 1% | Vishay | CRCW060350R0FKEA
1 | R208 | Resistor 0603 - 100Ohm - 1/10W - 1% | Vishay | CRCW0603100RFKEA
1 | R210 | Potentiometer - 100 Ohms - 25 turns - 10% - 0.5W - Bourns - 3296W-1-101LF | Bourns Electronics | 3296W-1-101LF
1 | R217 | Resistor 0603 - 28KOhm - 1/10W - 1% | Yageo | AC0603FR-0728KL | Panasonic | ERJ3EKF2802 | KOA Speer | RK73H1JHT..2802F
11 | R300, R302, R303, R310, R311, R314, R315, R336, R337, R344, R345 | Resistor 0603 - 0Ohm - 1/10W - 1% | Vishay | CRCW06030000FKEA
2 | R400, R603 | Resistor 0603 - 4.75KOhm - 1/10W - 1% | Vishay | CRCW06034K75FKEA
1 | S100 | Misc - Button - WURTH 430152080826 | Wurth Elektronik | 430152080826
1 | S200 | Slide switch - 4A - 30VDC - APEM - 25136NAH | APEM | 25136NAH
4 | S300, S301, S302, S303 | Misc - DIP switch - 8 rows - TE connectivity - 1825057-7 | TE Connectivity | 1825057-7
22 | THP200, THP201, THP202, THP203, THP204, THP205, THP206, THP207, THP208, THP209, THP210, THP300, THP301, THP302, THP303, THP304, THP305, THP306, THP309, THP310, THP311, THP312 | Misc - Test pin - Through hole - Millmax - 6821-0-00-15-00-00-08-0 | Mill-max | 6821-0-00-15-00-00-08-0
1 | U100 | FPGA - 1.2V - Altera - EP4CE22E22C6 | Altera | EP4CE22E22C6
1 | U105 | IC - Serial configuration device - 16Mbits - SOIC8 - Altera - EPCS168N | Altera / Intel | EPCS16SI8N | Altera / Intel | EPCQ16ASI8N
3 | U200, U202, U205 | Power - LDO - Adj - 20V - 1.5A - SOT223-6 | Texas Instruments | TL1963ADCQR
3 | U201, U204, U208 | Power - LDO - 3.3V - 300 mA - SOT23-5L | STMicroelectronics | LDK130M33R
1 | U203 | Power - Operationnal amplifier - ADA4895-1 | Analog Device | ADA4895-1ARJZ-R
1 | U206 | Power - LDO - 1.2V - 300 mA - SOT23-5L | STMicroelectronics | LDK130M12R
1 | U207 | Power - LDO - 2.5V - 300 mA - SOT23-5L | STMicroelectronics | LDK130M25R
1 | U400 | Power - LED Driver - 24 LEDs - TLC5952 - HTSSOP32 | Texas Instruments | TLC5952DAP
4 | U600, U601, U602, U604 | Logic - Level Shifter - 1.65V - 5.5V - 420Mbps -3-state - SOT23-6 - Texas Instruments - SN74LVC1T45DBVR | Texas Instruments | SN74LVC1T45DBVR
1 | U603 | IC - USB-to-UART 1-CH 256Byte FIFO - 5V - 28-Pin SSOP | FTDI | FT232RL
1 | Y100 | Oscillator - 25MHz - 3.3V - HCMOS - ECS-2520S33-250-FN-TR | ECS | ECS-2520S33-250-FN-TR

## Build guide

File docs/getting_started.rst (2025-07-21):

Getting started
===============

Scaffold is a FPGA board made for security research on hardware embedded
devices. It is capable of communicating with many circuits using standard
protocols. It can be easily extended with new protocols by writing new
transceivers in VHDL or Verilog language, and integrating it in the proposed
scaffold global architecture. When exchanging messages with the devices under
tests, Scaffold can generate triggers for chosen commands, spy data on a bus or
intercept and traffic.

Scaffold board also embeds special electronics tailored for hardware attacks:

- Sense resistor and analog amplifier for real-time current measurement
- FPGA safety protections against voltage glitch attacks
- Controllable power switches
- Fast power tearing capability, for emergency shutdown of the device under test
- Delay and pulse generators, allowing firing glitches or laser pulses.

An easy-to-use python API is provided to control the board. https://github.com/Ledger-Donjon/scaffold

Board tour
----------



- **A**: USB2 link with host computer. Also used to power the board.
- **B**: Main board power switch.
- **C**: Switch the jumper to the right to power the board from an external 5 V
  power supply and not from the USB.
- **D**: External power supply for the platform socket.
- **E**: External power supply for the DUT socket.
- **F**: Adjustable voltage regulator for the platform socket. When the jumper
  is set on top position, this power source is not used and the platform socket
  is powered from the external power supply.
- **G**: Adjustable voltage regulator for the DUT socket. When the jumper is set
  on top position, this power source is not used and the DUT socket is powered
  from the external power supply.
- **H**: Adjustable voltage regulator for the I/O bank of the FPGA connected to
  the platform and DUT sockets. This allows setting the correct voltage
  depending on the connected device. Supported voltage range goes from 1.5 V up
  to 3.3 V.
- **I**: FPGA active serial connector for bitstream programmation. An USB
  blaster can be used to update the bitstream.
- **J**: FPGA reset button. Push if the board enters error state.
- **K**: Switches to select Spy or Intercept mode for each I/O of the FPGA. In
  intercept mode, the signals of the platform and DUT sockets are not connected
  anymore and the FPGA can act as a man in the middle circuit.
- **L**: Switches to enable 1 KOhm series protection resistors on the I/Os (at
  the cost of slew-rate). Shall be enabled when there is a risk to damage the
  FPGA, with high-voltage glitches for instance.
- **M**: Tearing input. Any positive edge will power-off the DUT immediately and
  shunt all I/Os to ground.
- **N**: A0, A1, A2, A3 voltage standard selection between 3.3 V or 5 V. Move
  the jumper to change the voltage of the corresponding I/O.
- **O**: I/Os with voltage translators. 5 V is suited to drive Alphanov TTL
  50 Ohm laser sources (other 3.3 V I/Os can't).
- **P**: FPGA I/Os. Maximum voltage is 3.3 V. Those I/Os are connected to the
  platform and DUT sockets and are usually used to communicate with the target
  device and generate triggers. SMA connectors are provided for D0 to D6.
- **Q**: Platform socket and power state LED.
- **R**: DUT socket and power state LED.
- **S**: Adjustable shunt resistor for power trace measurement.
- **T**: Output of the analog 11 X amplifier for power trace measurement.

Connecting the board
--------------------

Connect the board with a micro-USB cable to your computer. Power-on the board
using the power switch. The operating system shall detect the board as a
USB-To-Serial device (COMx on Windows, /dev/ttyUSBx on linux). It may be
necessary to install FTDI driver for some Windows versions.

Installation
------------

Python3 API library can be installed using pip3:

.. code-block:: bash

    pip3 install donjon-scaffold

Using the Python API
--------------------

The following example shows how to transmit for data using a UART peripheral of
Scaffold.

.. code-block:: python
    
    from scaffold import Scaffold

    # Connect to the board.
    # This will open the serial device and check for hardware version
    # Passing the serial device path is optional. If not specified, the library
    # will try to find the board automatically if not specified.
    scaffold = Scaffold('/dev/ttyUSB0')

    # Configure UART0 for operation
    uart = scaffold.uart0
    uart.baudrate = 115200

    # Connect UART0 signals to board pins
    # << operator connects signals. Left operand is the destination, right operand
    # is the source (the order is important)
    # In this example, D0 and D1 are configured as outputs, D2 is configured as an
    # input.
    scaffold.d0 << uart.tx
    scaffold.d1 << uart.trigger
    uart.rx << scaffold.d2

    # UART is now ready to use
    uart.transmit('Hello world !'.encode(), trigger=True)

Using the Command-Line-Interface
--------------------------------

The Python3 API also provides a command-line interface (CLI) for quick Scaffold
interaction and scripting without writing Python code.

To get global help and see available modules, run:

.. code-block:: bash

  scaffold -h

To get help on a specific module, use:

.. code-block:: bash

  scaffold <module> -h

Available modules are:

- power: manage power state of the DUT and platform (and setup triggers)
- io: manage I/O pins power state
- uart: receive and transmit UART messages
- iso7816: send APDUs to smartcards 
- version: display the scaffold version
- list: list connected Scaffold boards

Typical usage examples:

- list connected Scaffold boards:

  .. code-block:: bash

    scaffold list

- power on the DUT with a trigger on d4:

  .. code-block:: bash

    scaffold power dut on --trigger d4

- change state of the platform I/O d0 to high:

  .. code-block:: bash

    scaffold io d0 high

- get an interactive UART shell (rx and tx connected to d1 and d0) with a baudrate of 115200:

  .. code-block:: bash

    scaffold --dev /dev/ttyUSB0 uart d1 d0 --baudrate 115200 --mode repl

- send an APDU command to a smartcard:

  .. code-block:: bash

    scaffold iso7816 apdu 00b2000000

Refer to the CLI help for more options and details on each command.

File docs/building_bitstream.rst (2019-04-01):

Building and flashing the FPGA bitstream
========================================

Advanced users may want to modify the architecture of the FPGA of Scaffold to
support more peripherals, implement new features or even fix bugs. This section
briefly describe how to build the FPGA bitstream with Intel (Altera) tools, and
flash the board.

Prerequisites
-------------

*Quartus II* software from Intel (Altera) must be used to build the FPGA
bitstream. The version of Quartus must have support for Cyclone IV devices;
version 14.1 can be used. Although *Quartus* is a proprietary tool, the free
*Quartus Web Edition* can be used and shall not require any license. Quartus
can run on linux and Windows (but we did not give a try on Windows).

For flashing the FPGA, a programmer supporting *Active Serial* mode must be
used. *Altera USB Blaster* is a good one.

Building the bitstream
----------------------

Under *Quartus* software, load the ``fpga-arch/scaffold.qpf`` project file with
the *File > Open Project* menu. Build the design with *Start* context-menu of
*Compile Design* task as highlighted below.

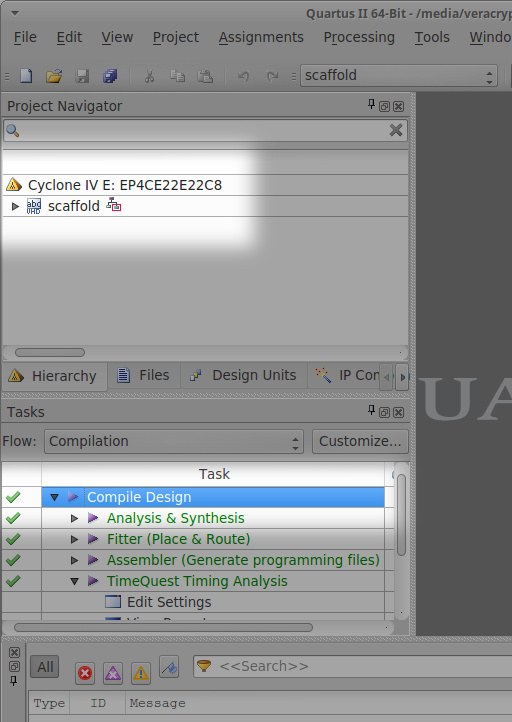
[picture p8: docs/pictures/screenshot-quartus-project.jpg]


Hopefully the compilation should succeed. If you modified the original design,
we recommand you to check in the compilation report that the max frequency of
the system clock of the compiled design is at least 110 MHz (100 MHz plus some
security margin). If this constraint is not respected, then your design may not
work properly and need to be optimized.

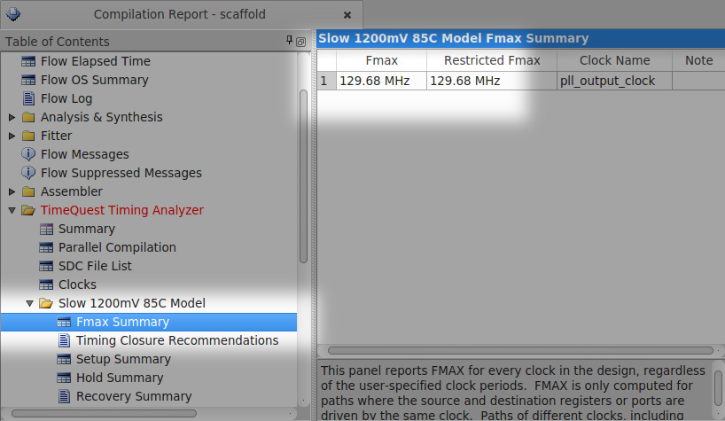
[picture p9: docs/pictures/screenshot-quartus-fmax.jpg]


Flashing the FPGA
-----------------

Power-on the board and connect the programmer as shown below:

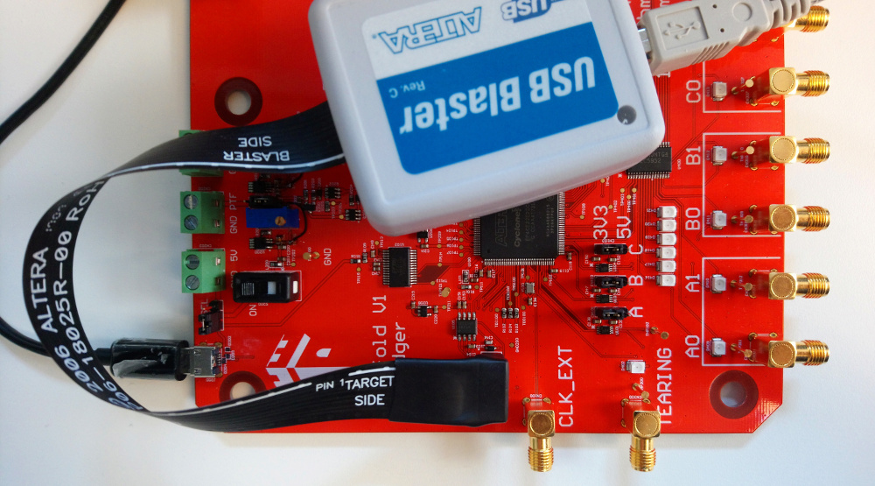
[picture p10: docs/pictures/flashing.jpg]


In *Quartus*, open the programmer window with the *Tools > Programmer* menu.

- Setup your programmer with the *Hardware Setup* button.
- Switch to *Active Serial Programming* mode.

- Click on *Add File...* and select the file ``confware.pof``. The setup shall
  represent an EPCS16 device, which is the on-board Flash memory storing the
  bitstream and read by the FPGA when powering-up Scaffold.

- Check the *Program/Configure* and *Verify* boxes.
- Click on the *Start* button.

Remove the programmer cable to test your new design!

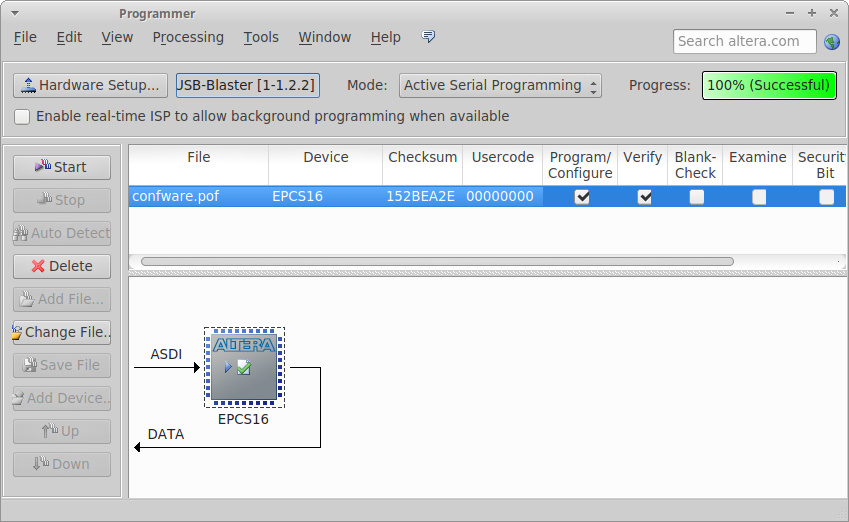
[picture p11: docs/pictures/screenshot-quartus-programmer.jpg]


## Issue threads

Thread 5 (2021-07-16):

### ISSUE TITLE
Avoiding the program to crash when the `/usr/share/pcsc/smartcard_list.txt` file cannot be found when calling the `find_info()` function.

### ISSUE THREAD

**Issue by T-TROUCHKINE** [Ledger-Donjon/scaffold#5]
Hello,

I think it is interesting to avoid the crash of the program when the `/usr/share/pcsc/smartcard_list.txt` file cannot be found while calling the `find_info()` function as it is system dependent and avoid the example `secaes-atmega.py` to work out of the box.

It may also be interesting to customize the location of this file or even be able to directly fetch it online.

Regards !

**Comment by kingofpayne** [comment]
Missing the ATR list file should not be silent, we want users to be aware it must be installed.
Maybe a good solution would be to raise a `MissingATRDatabase` exception and print warning message in the example files to prevent crashes.

For the customization part, I propose to add an optional argument to the `find_info` method so the user can pass a path to the file directly.

About fetching the file online, we can try that as a fallback when the list is not installed and when the user did not supply a path to the file.

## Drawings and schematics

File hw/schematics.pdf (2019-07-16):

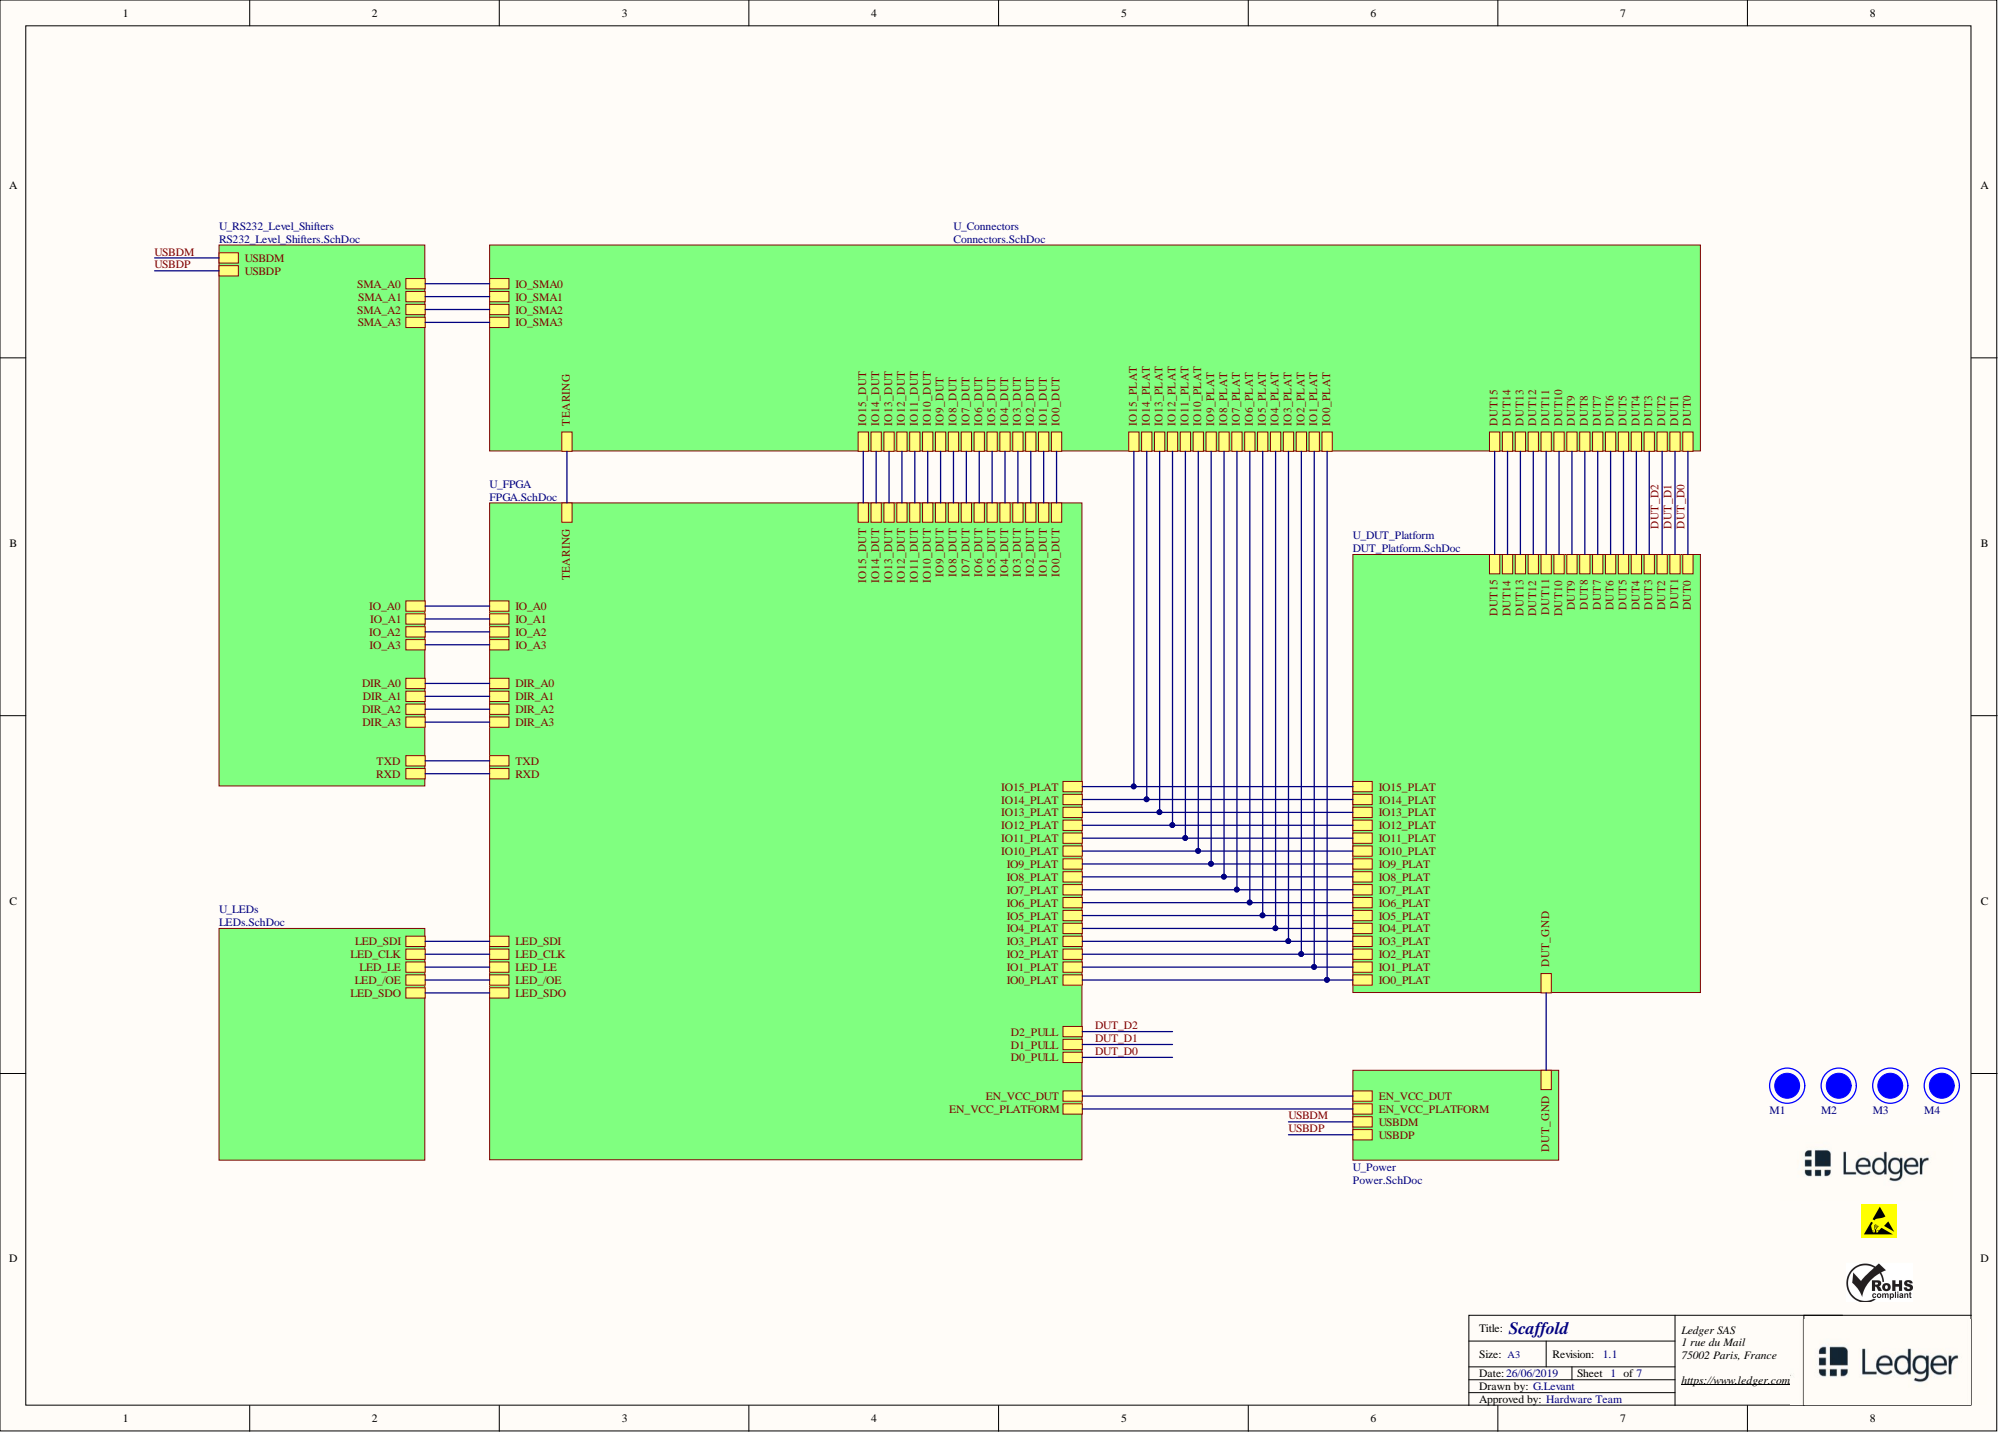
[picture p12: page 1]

Scaffold Title: | Ledger SAS 1 rue du Mail 75002 Paris, France

Size: A3 | Revision:
Date: | Sheet of | https://www.ledger.com/ 7

Drawn by:
Approved by: Hardware Team

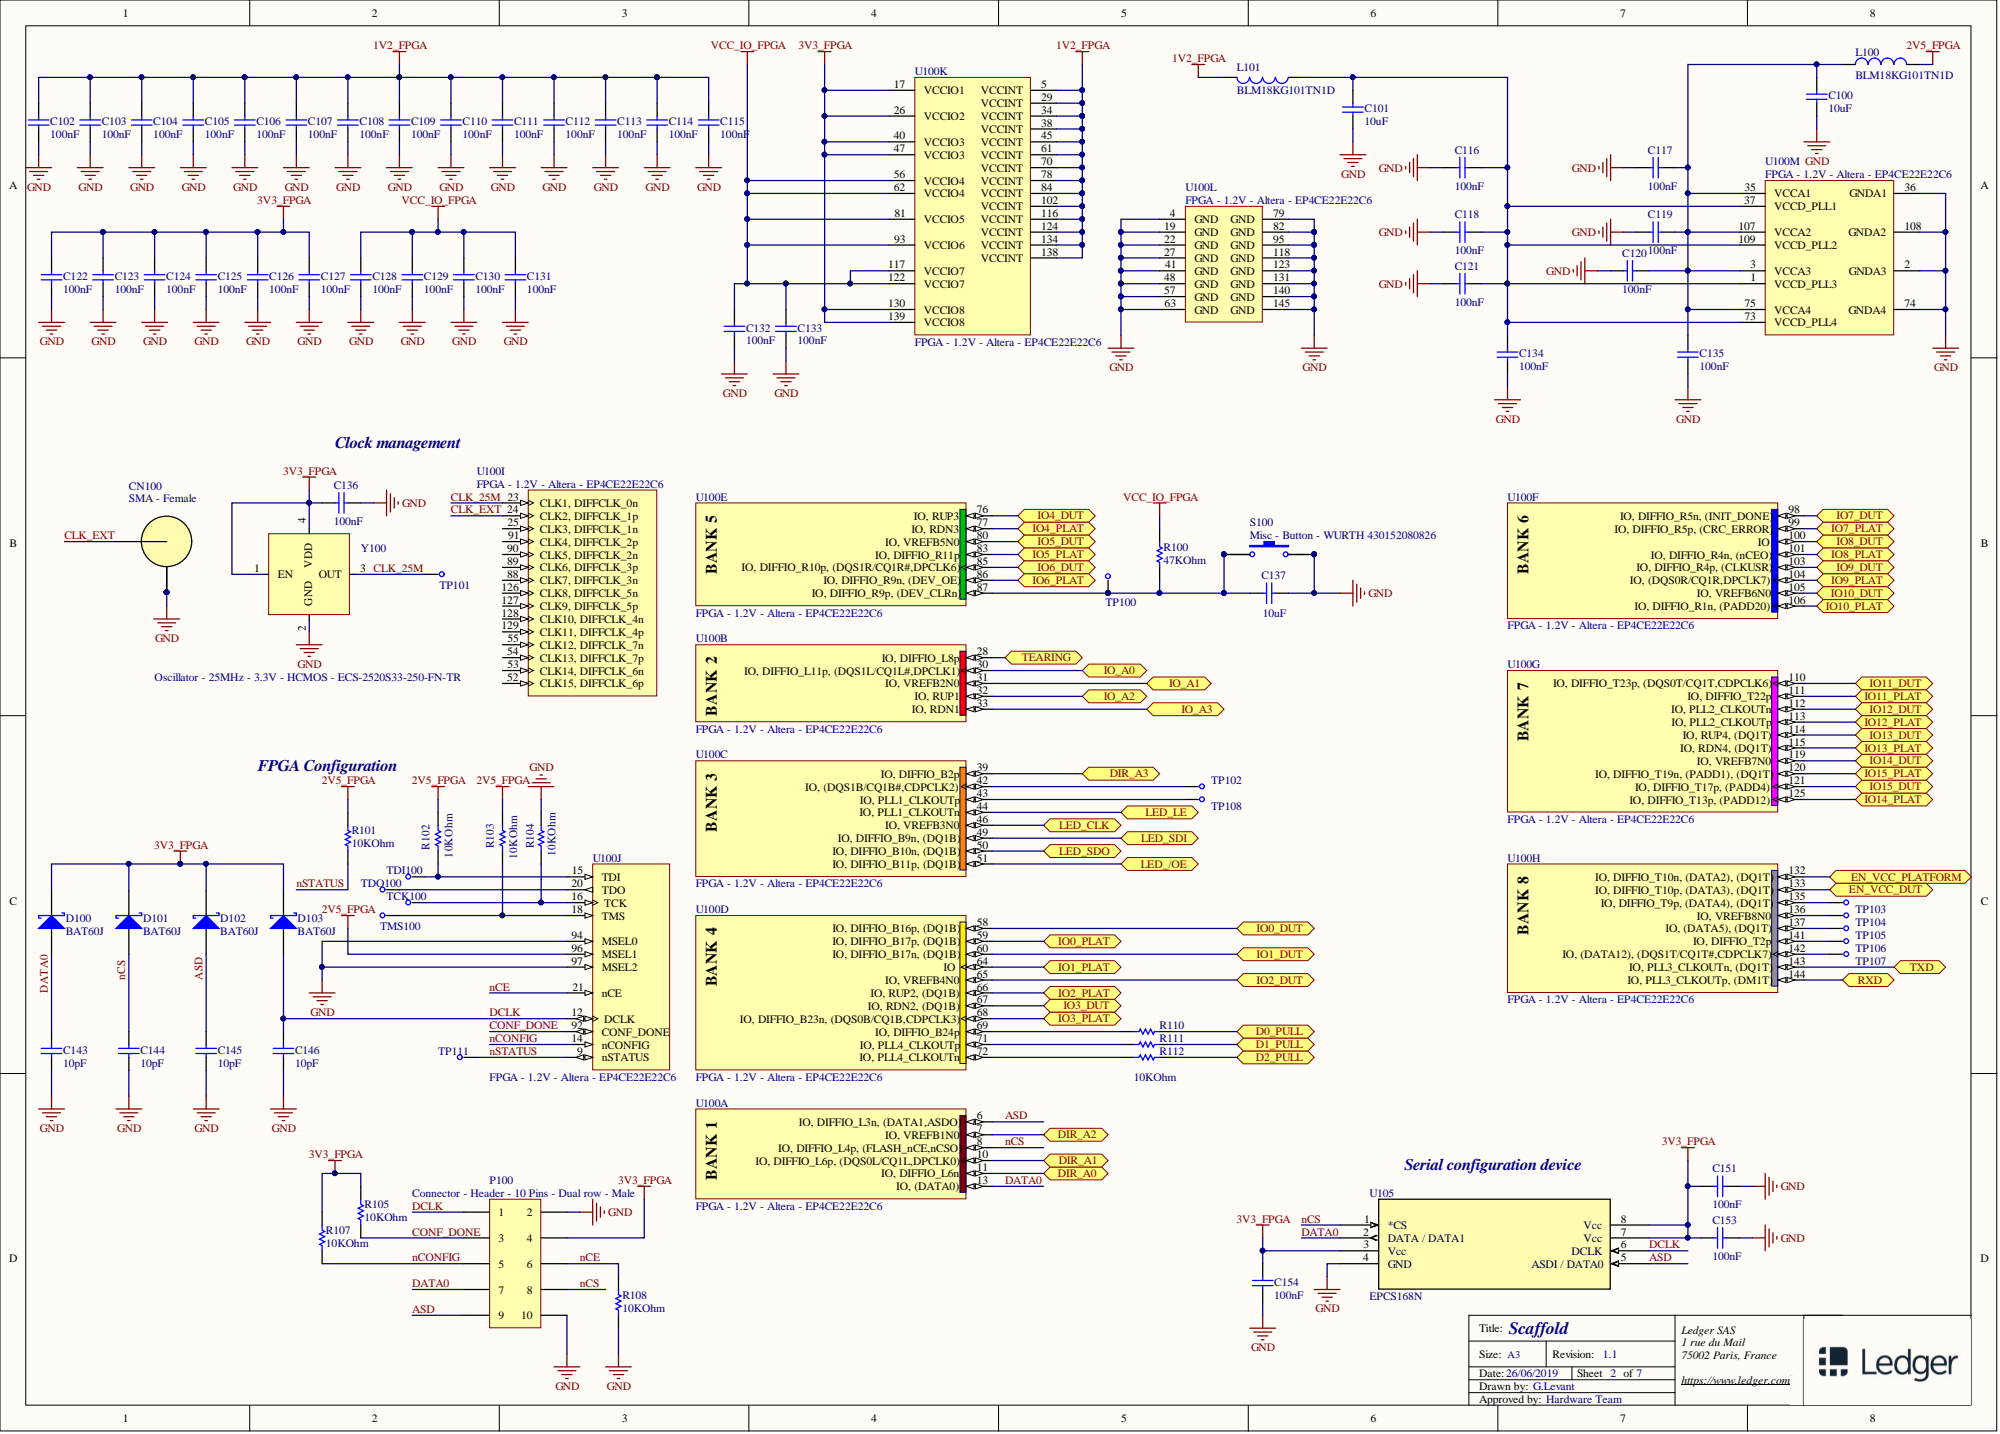
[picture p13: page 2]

Oscillator - 25MHz - 3.3V - HCMOS - ECS-2520S33-250-FN-TR

Connector - Header - 10 Pins - Dual row - Male
DCLK

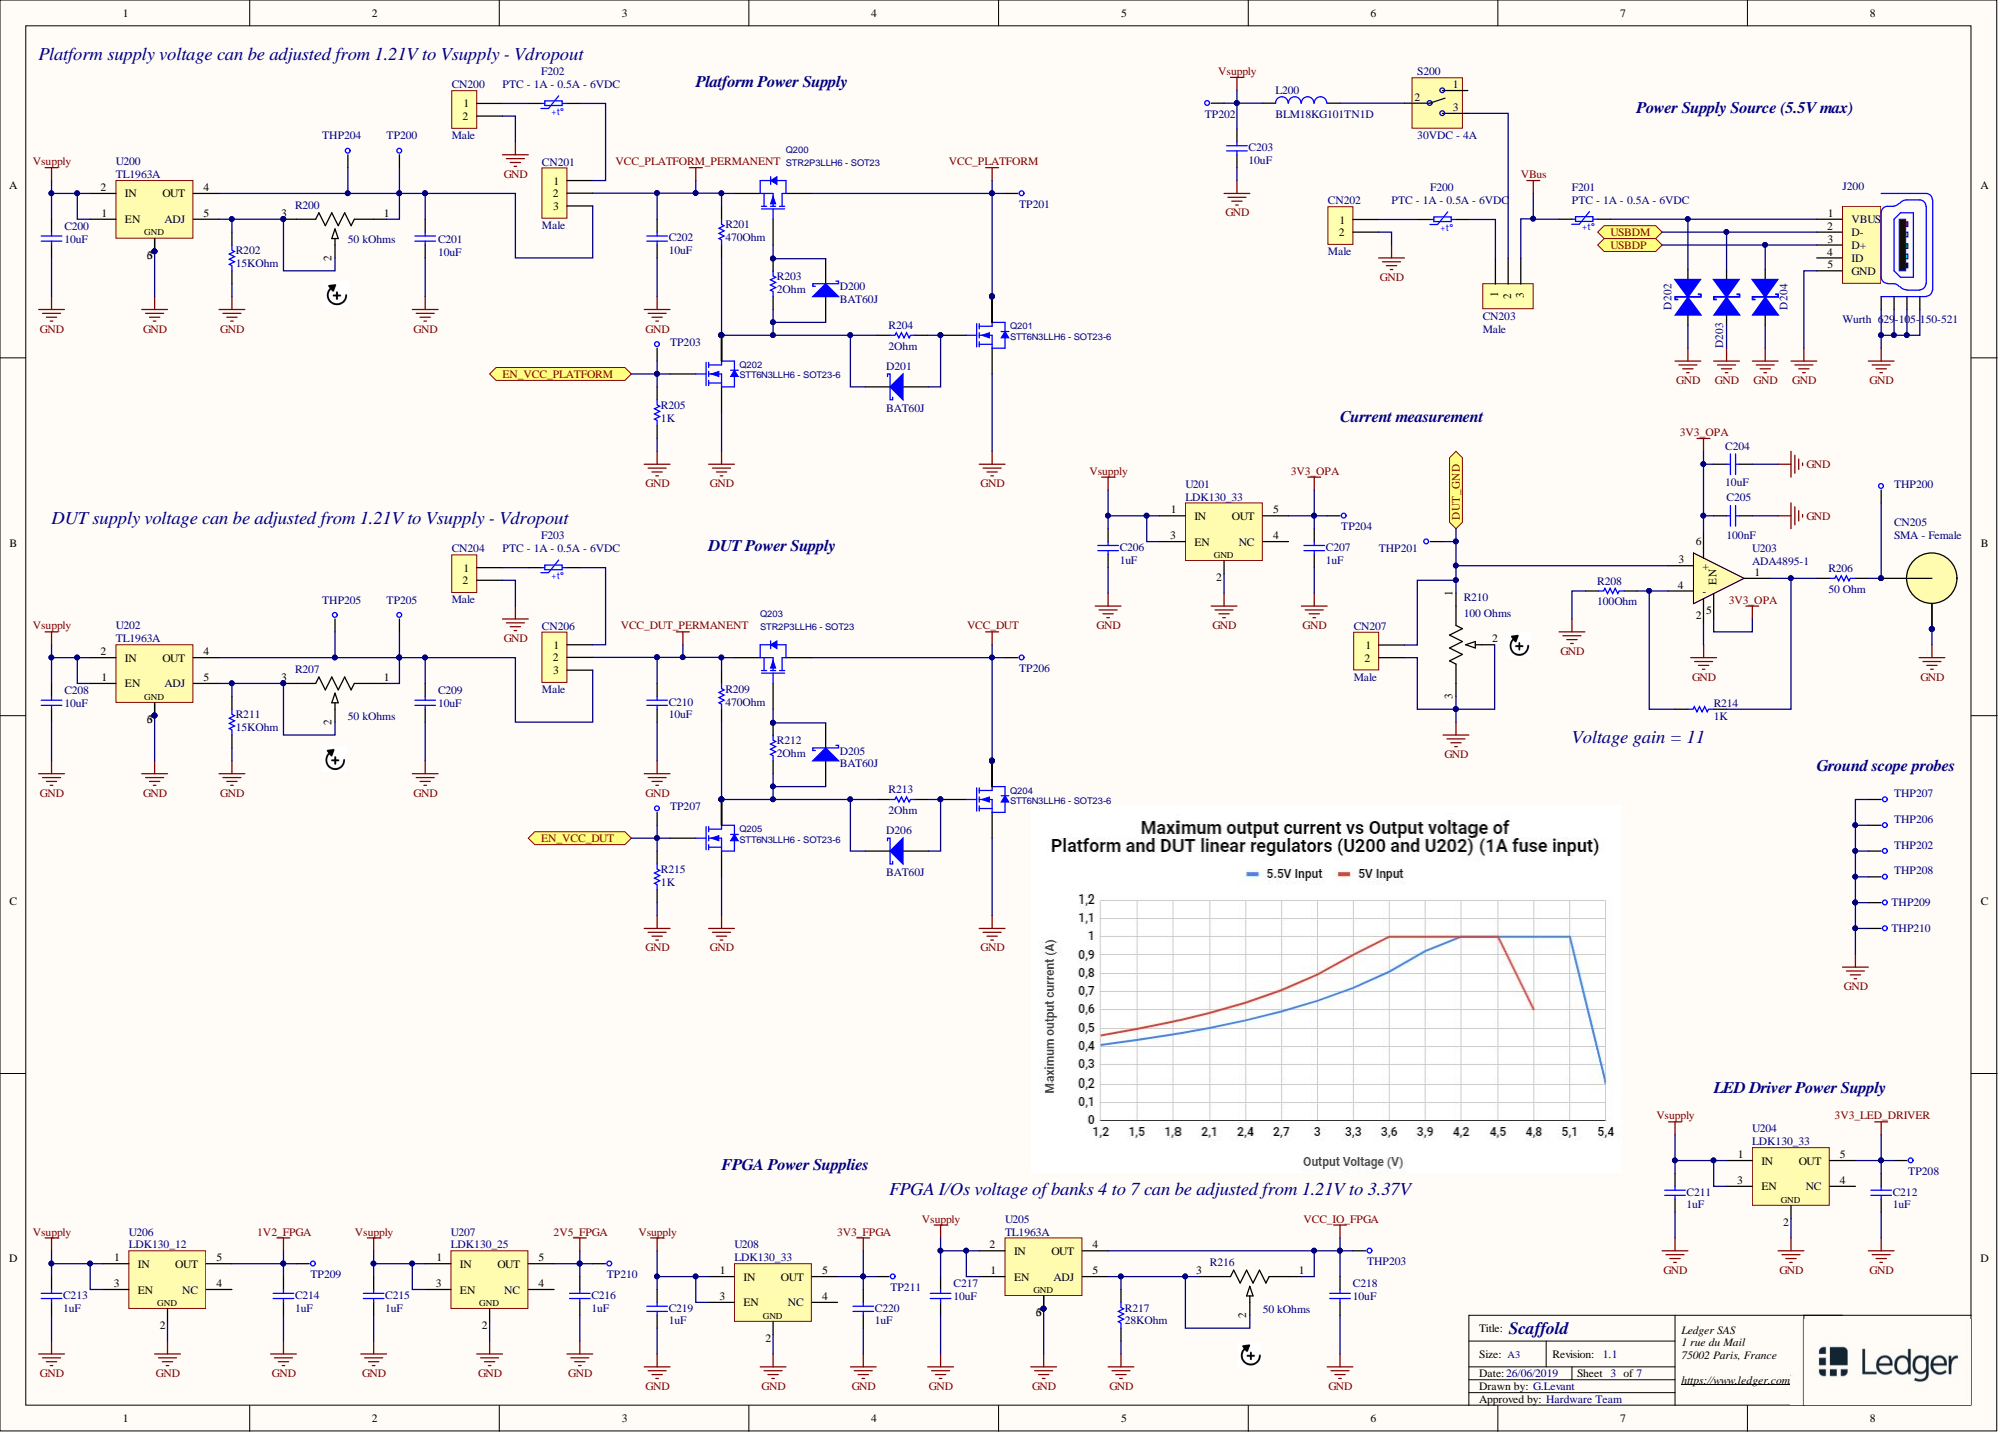
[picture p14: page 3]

Platform supply voltage can be adjusted from 1.21V to Vsupply - Vdropout

Power Supply Source (5.5V max)

DUT supply voltage can be adjusted from 1.21V to Vsupply - Vdropout

LED Driver Power Supply

FPGA I/Os voltage of banks 4 to 7 can be adjusted from 1.21V to 3.37V

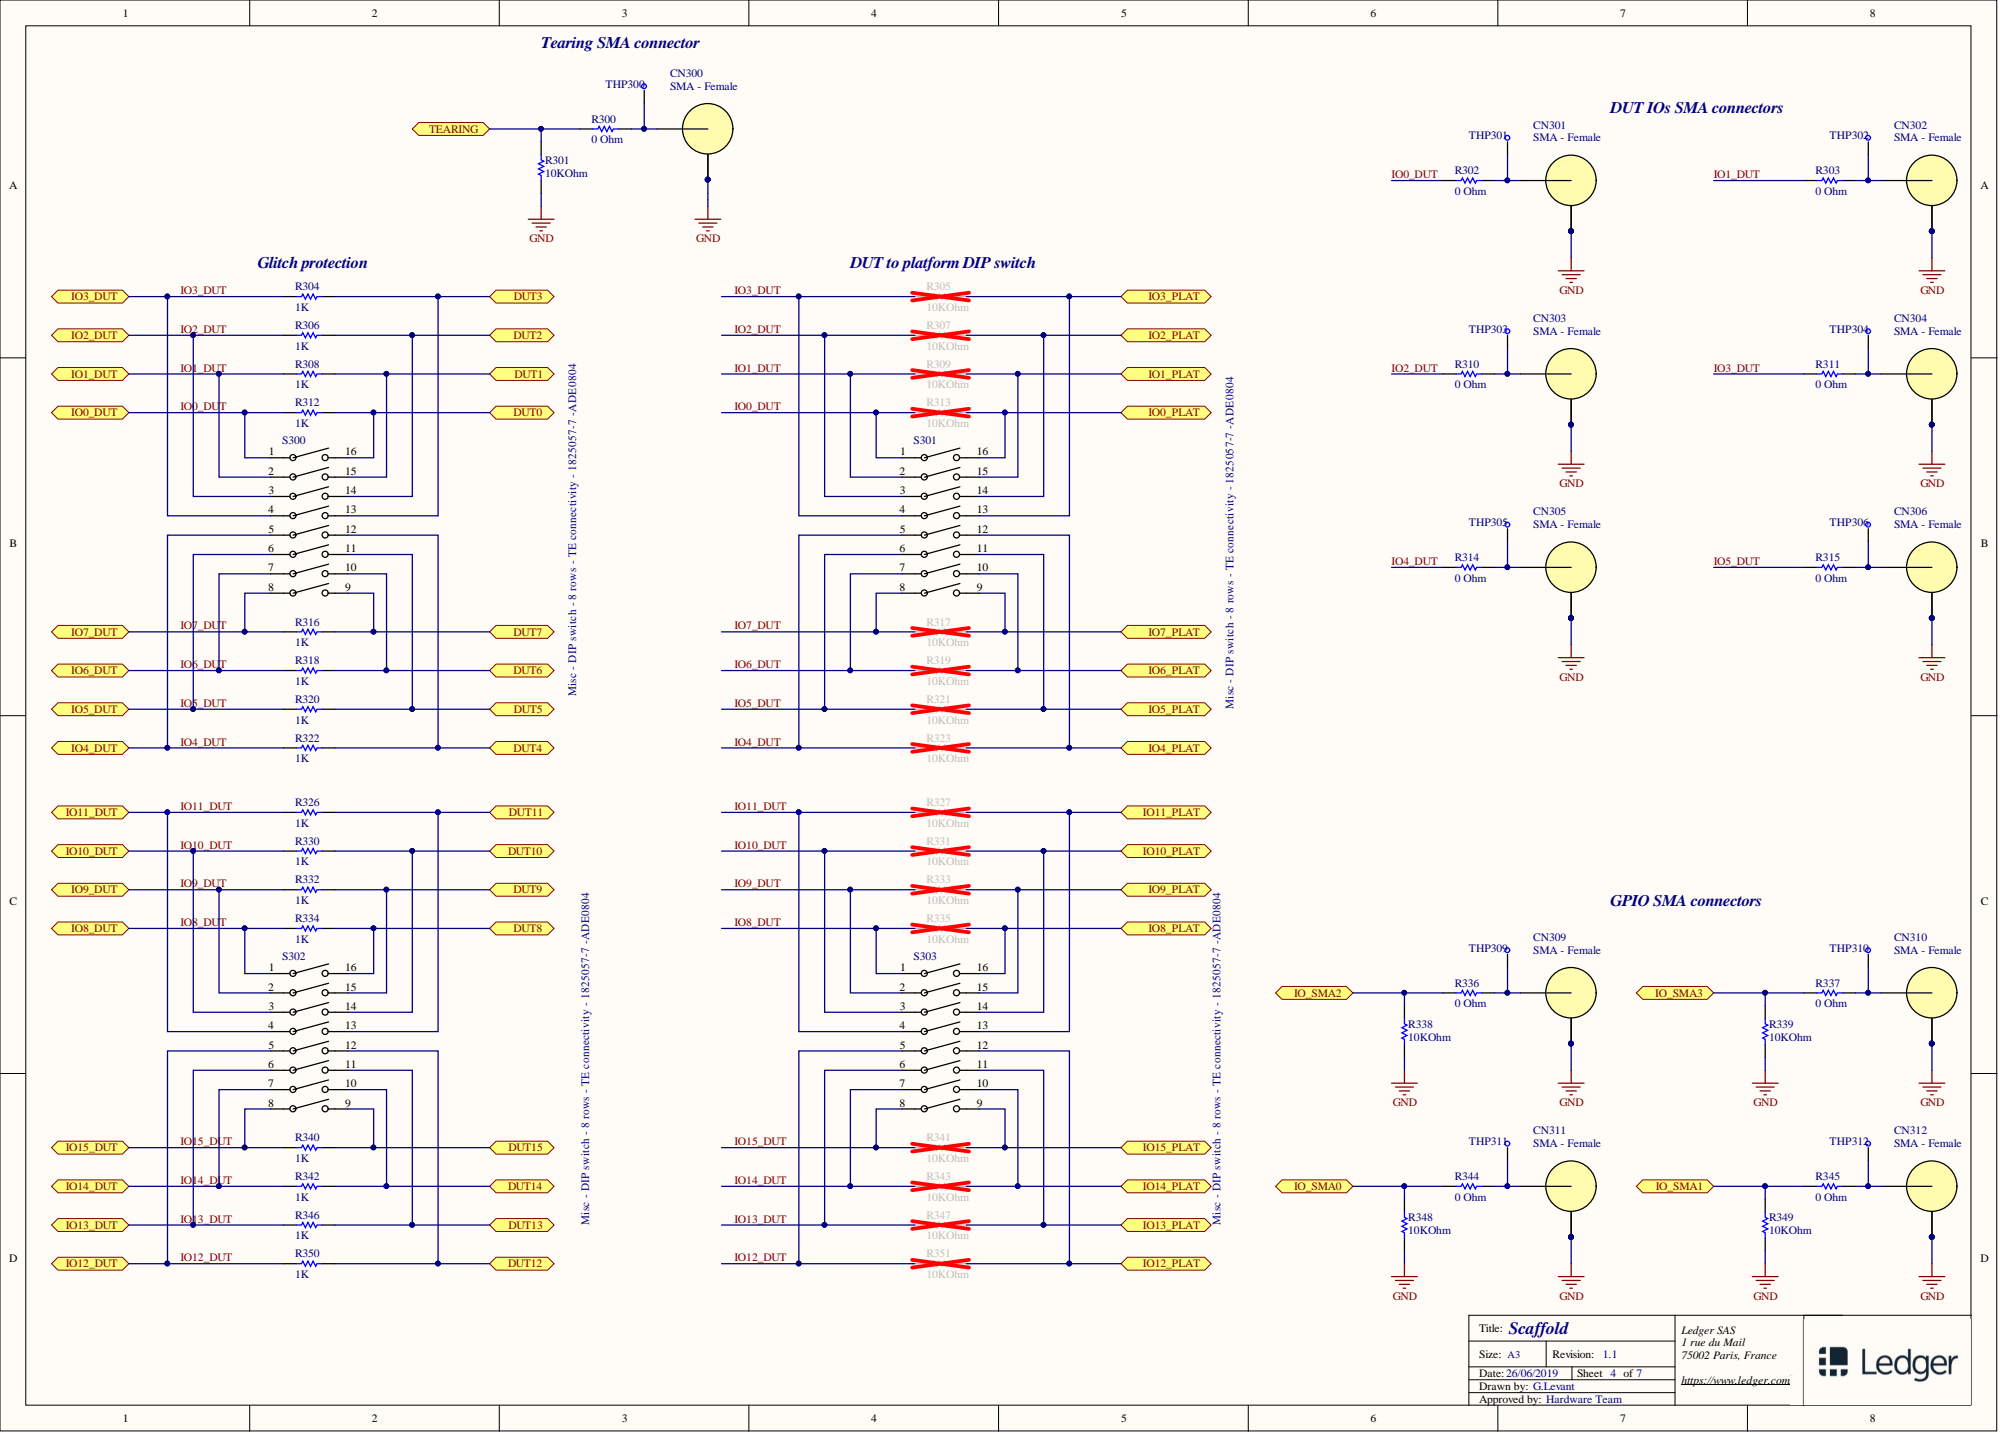
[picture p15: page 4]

DUT IOs SMA connectors

DUT to platform DIP switch

Misc - DIP switch - 8 rows - TE connectivity - 1825057-7 -ADE0804

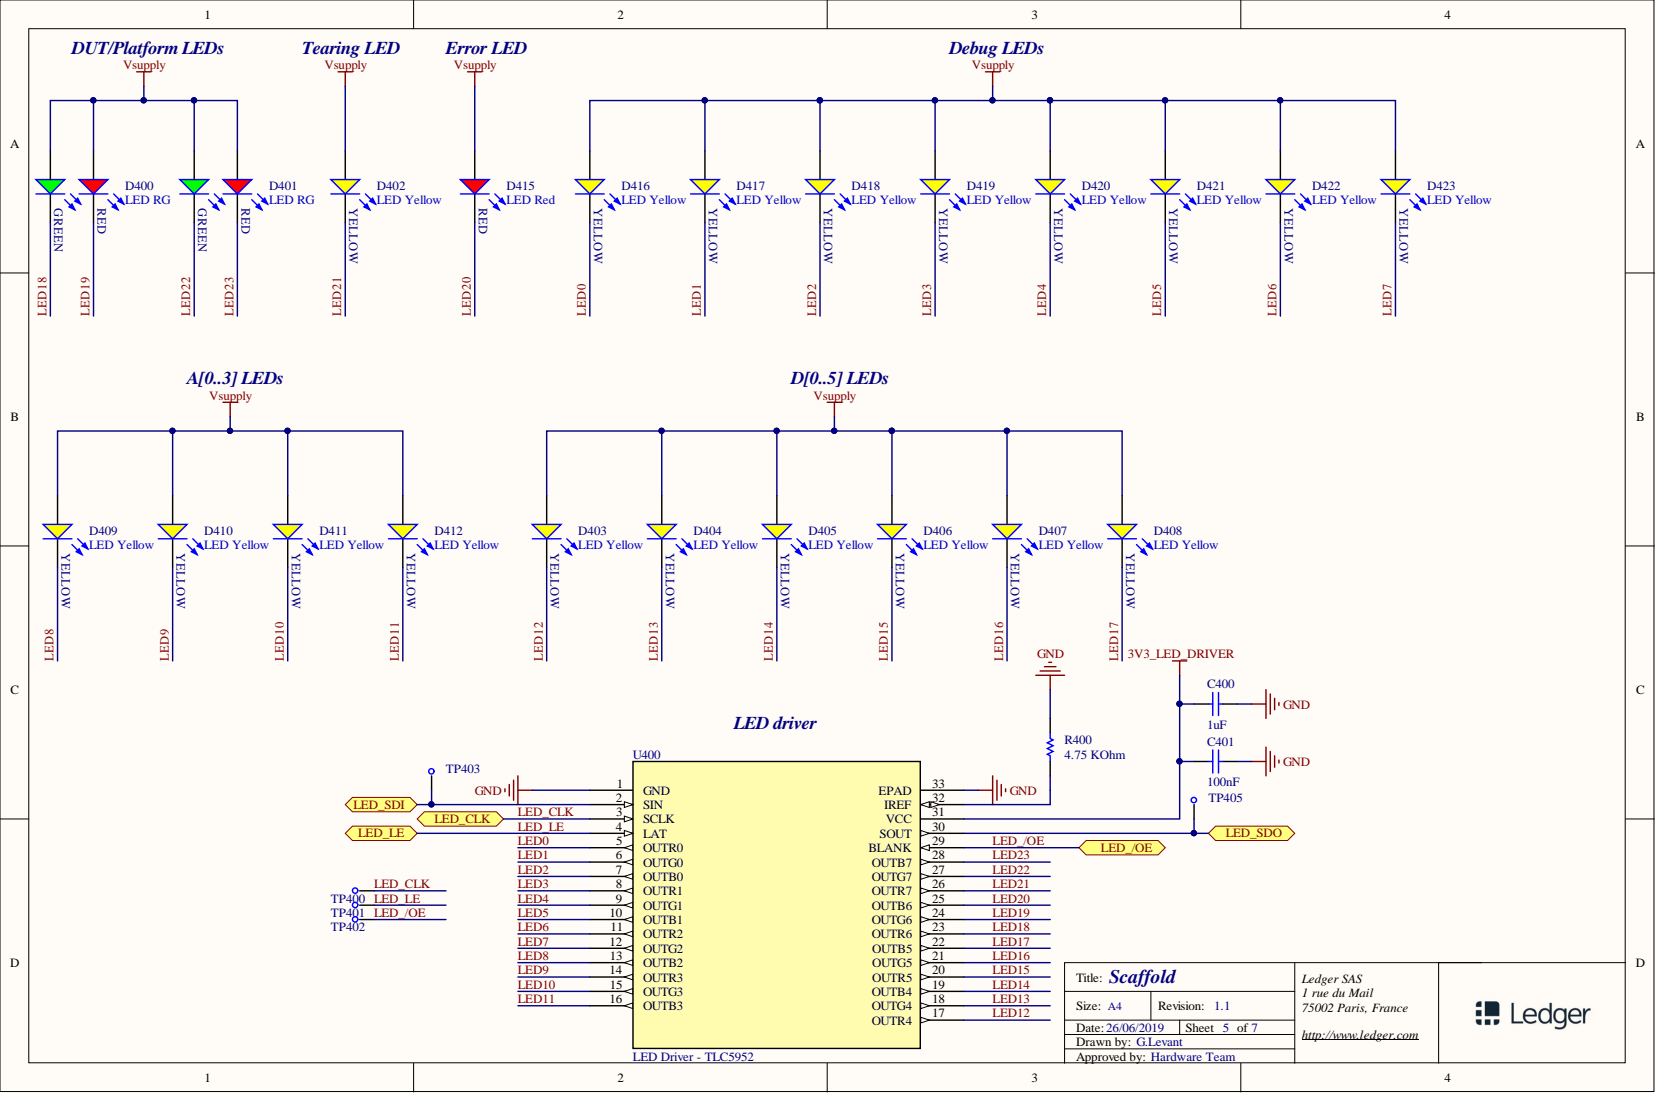
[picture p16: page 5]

http://www.ledger.com 7

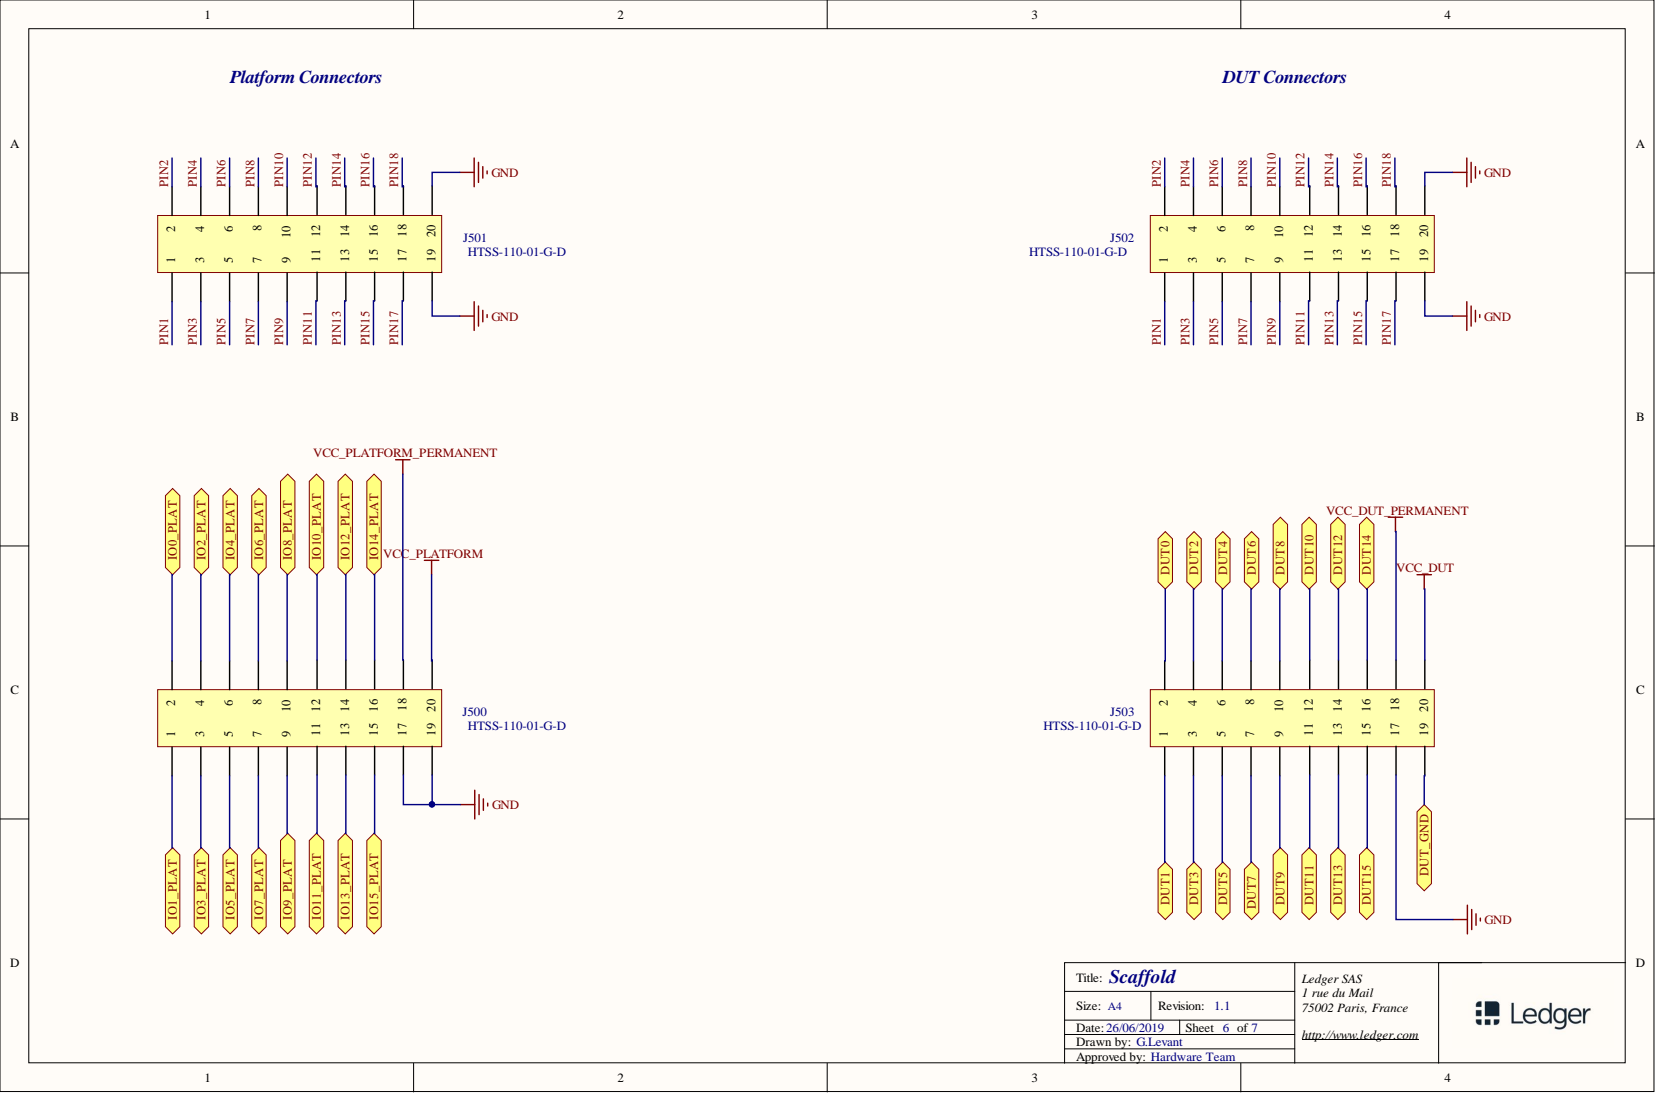
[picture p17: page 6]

Titl e : S caffold | L e dg er SAS 1 r u e d u Ma i l Paris, Fra n c e http://www. l e dge r. com

S i z e : | R e visi o n : .

Date : 26/ 06/ | S h e e t o f

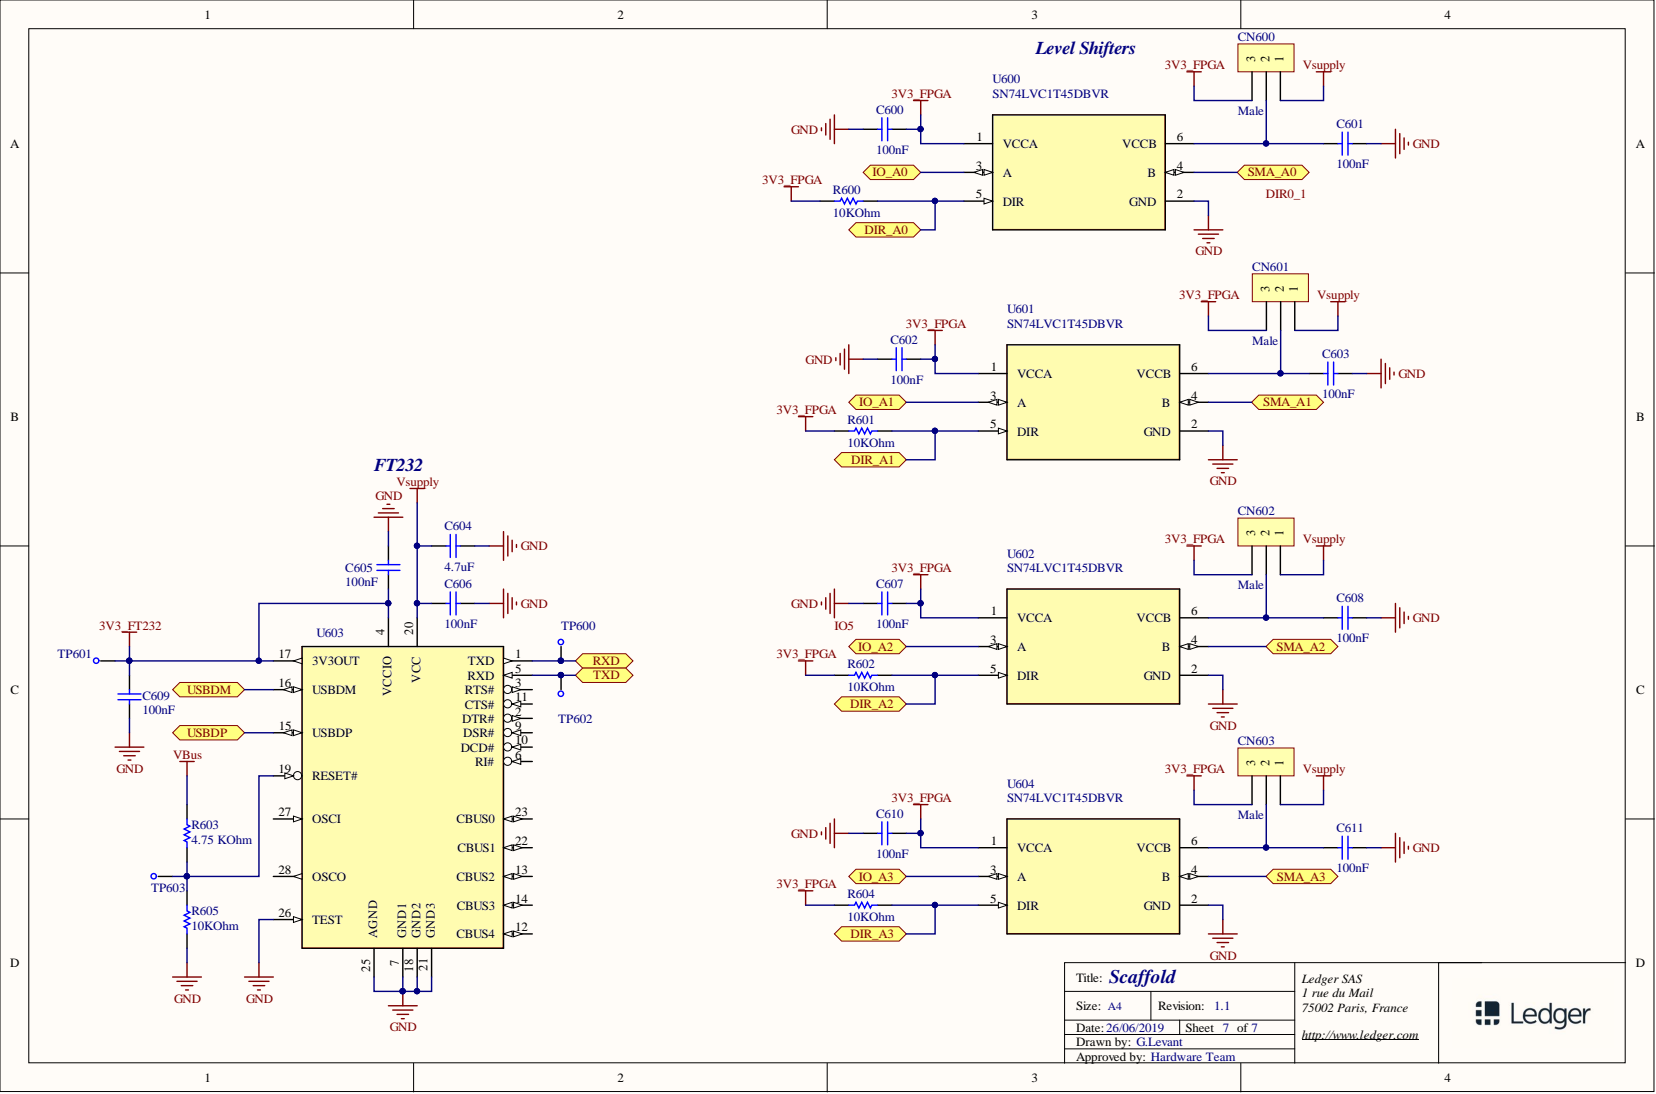
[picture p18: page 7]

http://www.ledger.com 7

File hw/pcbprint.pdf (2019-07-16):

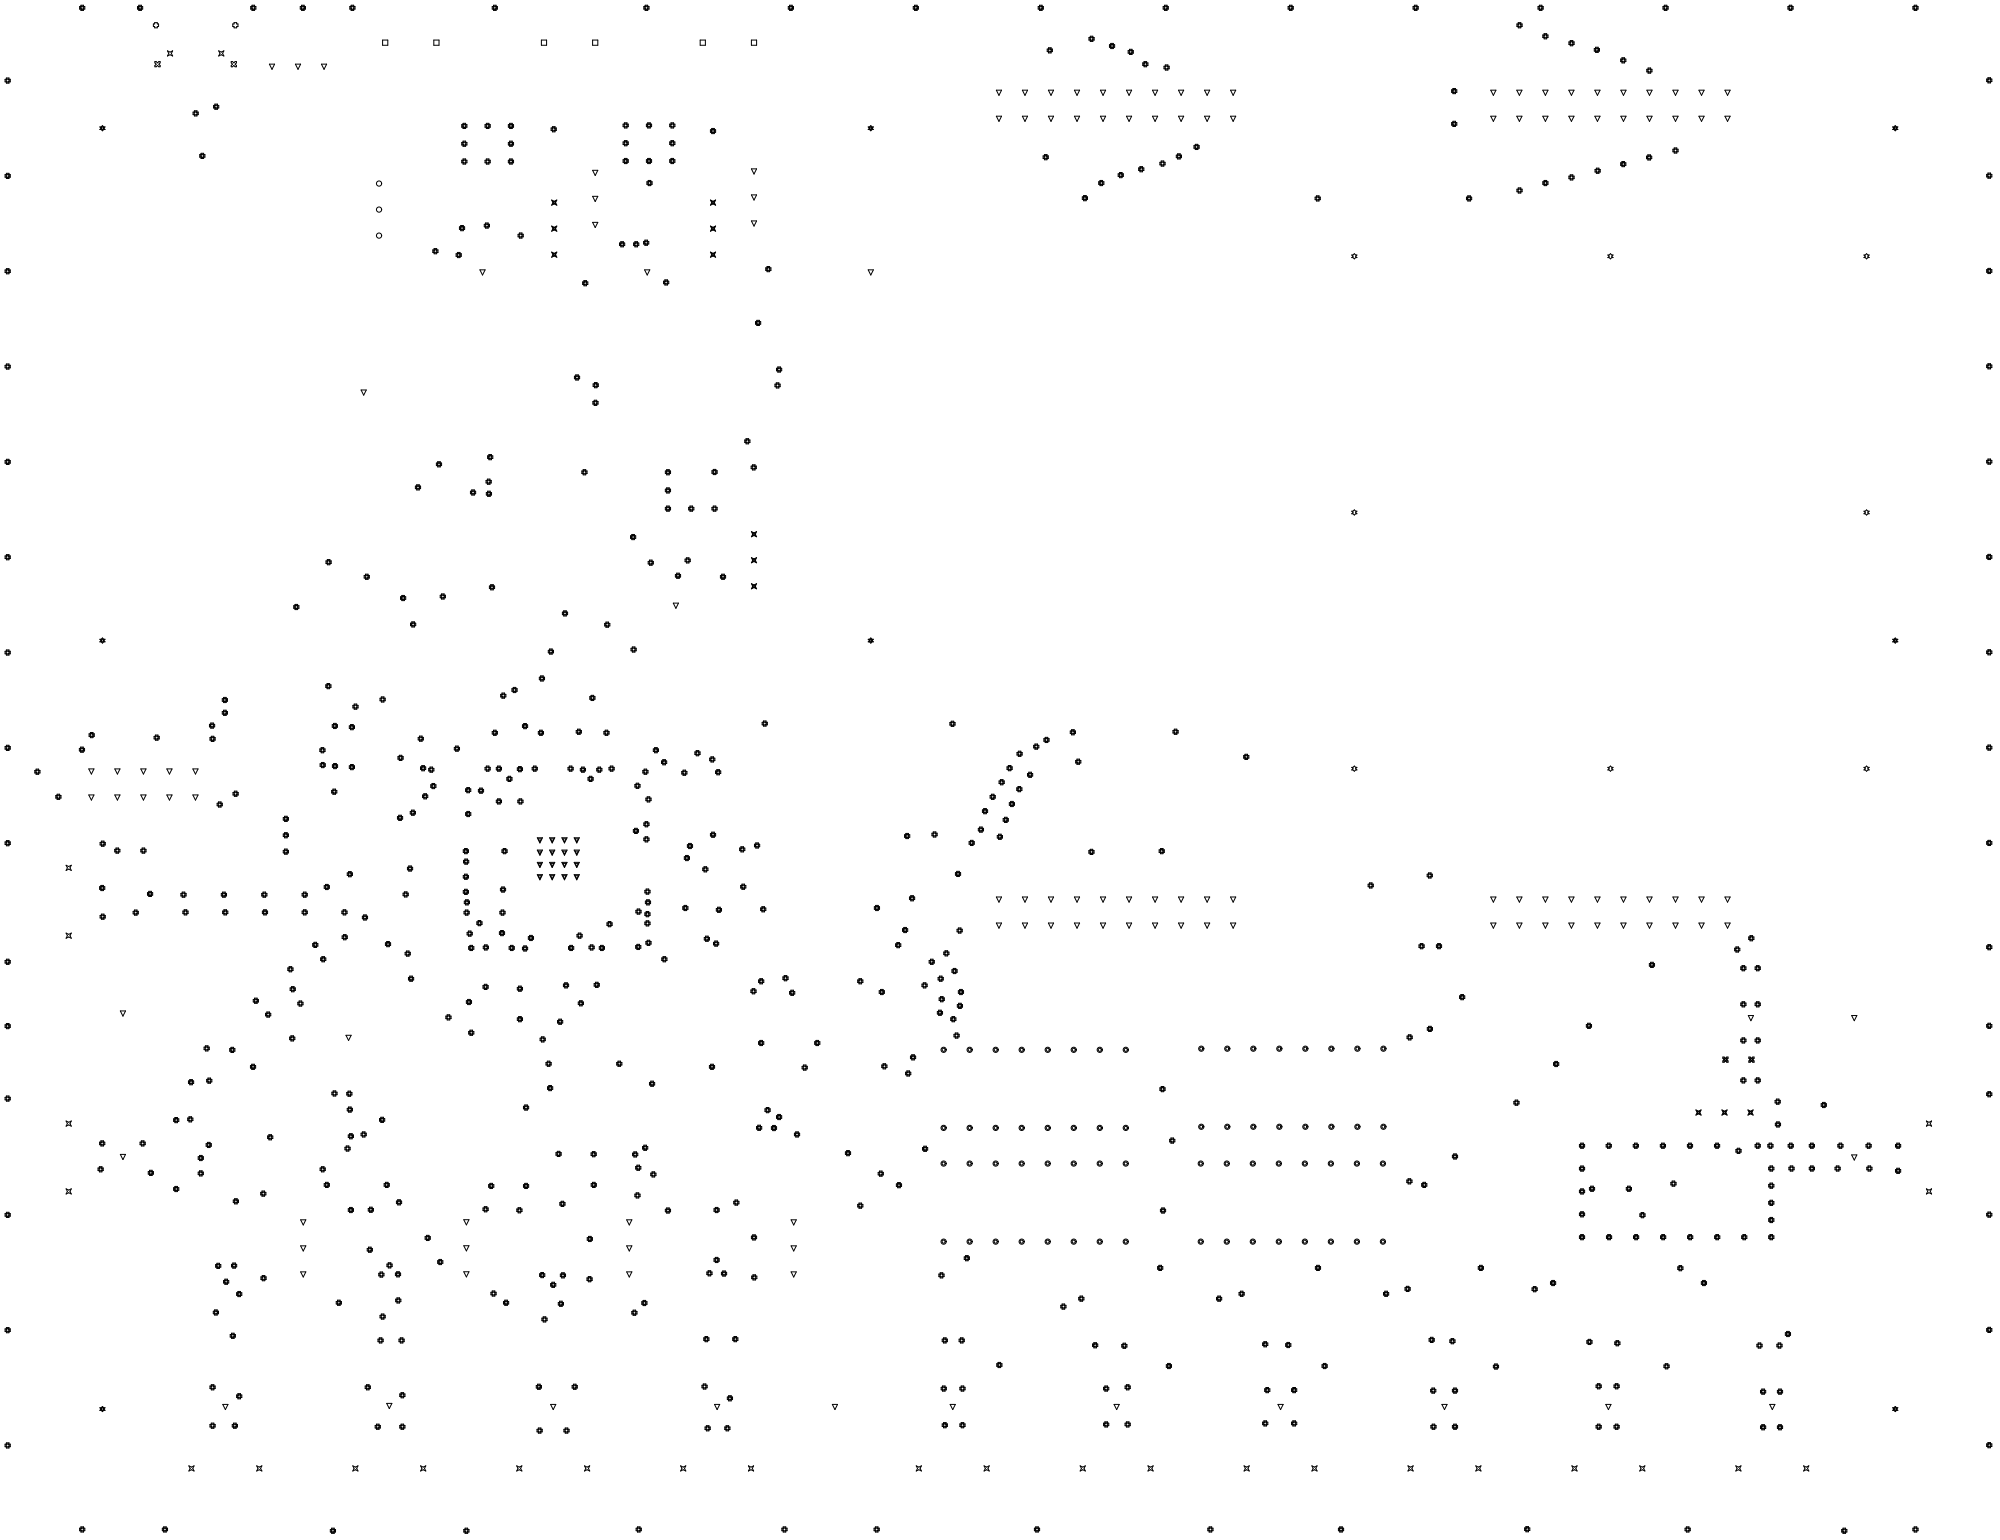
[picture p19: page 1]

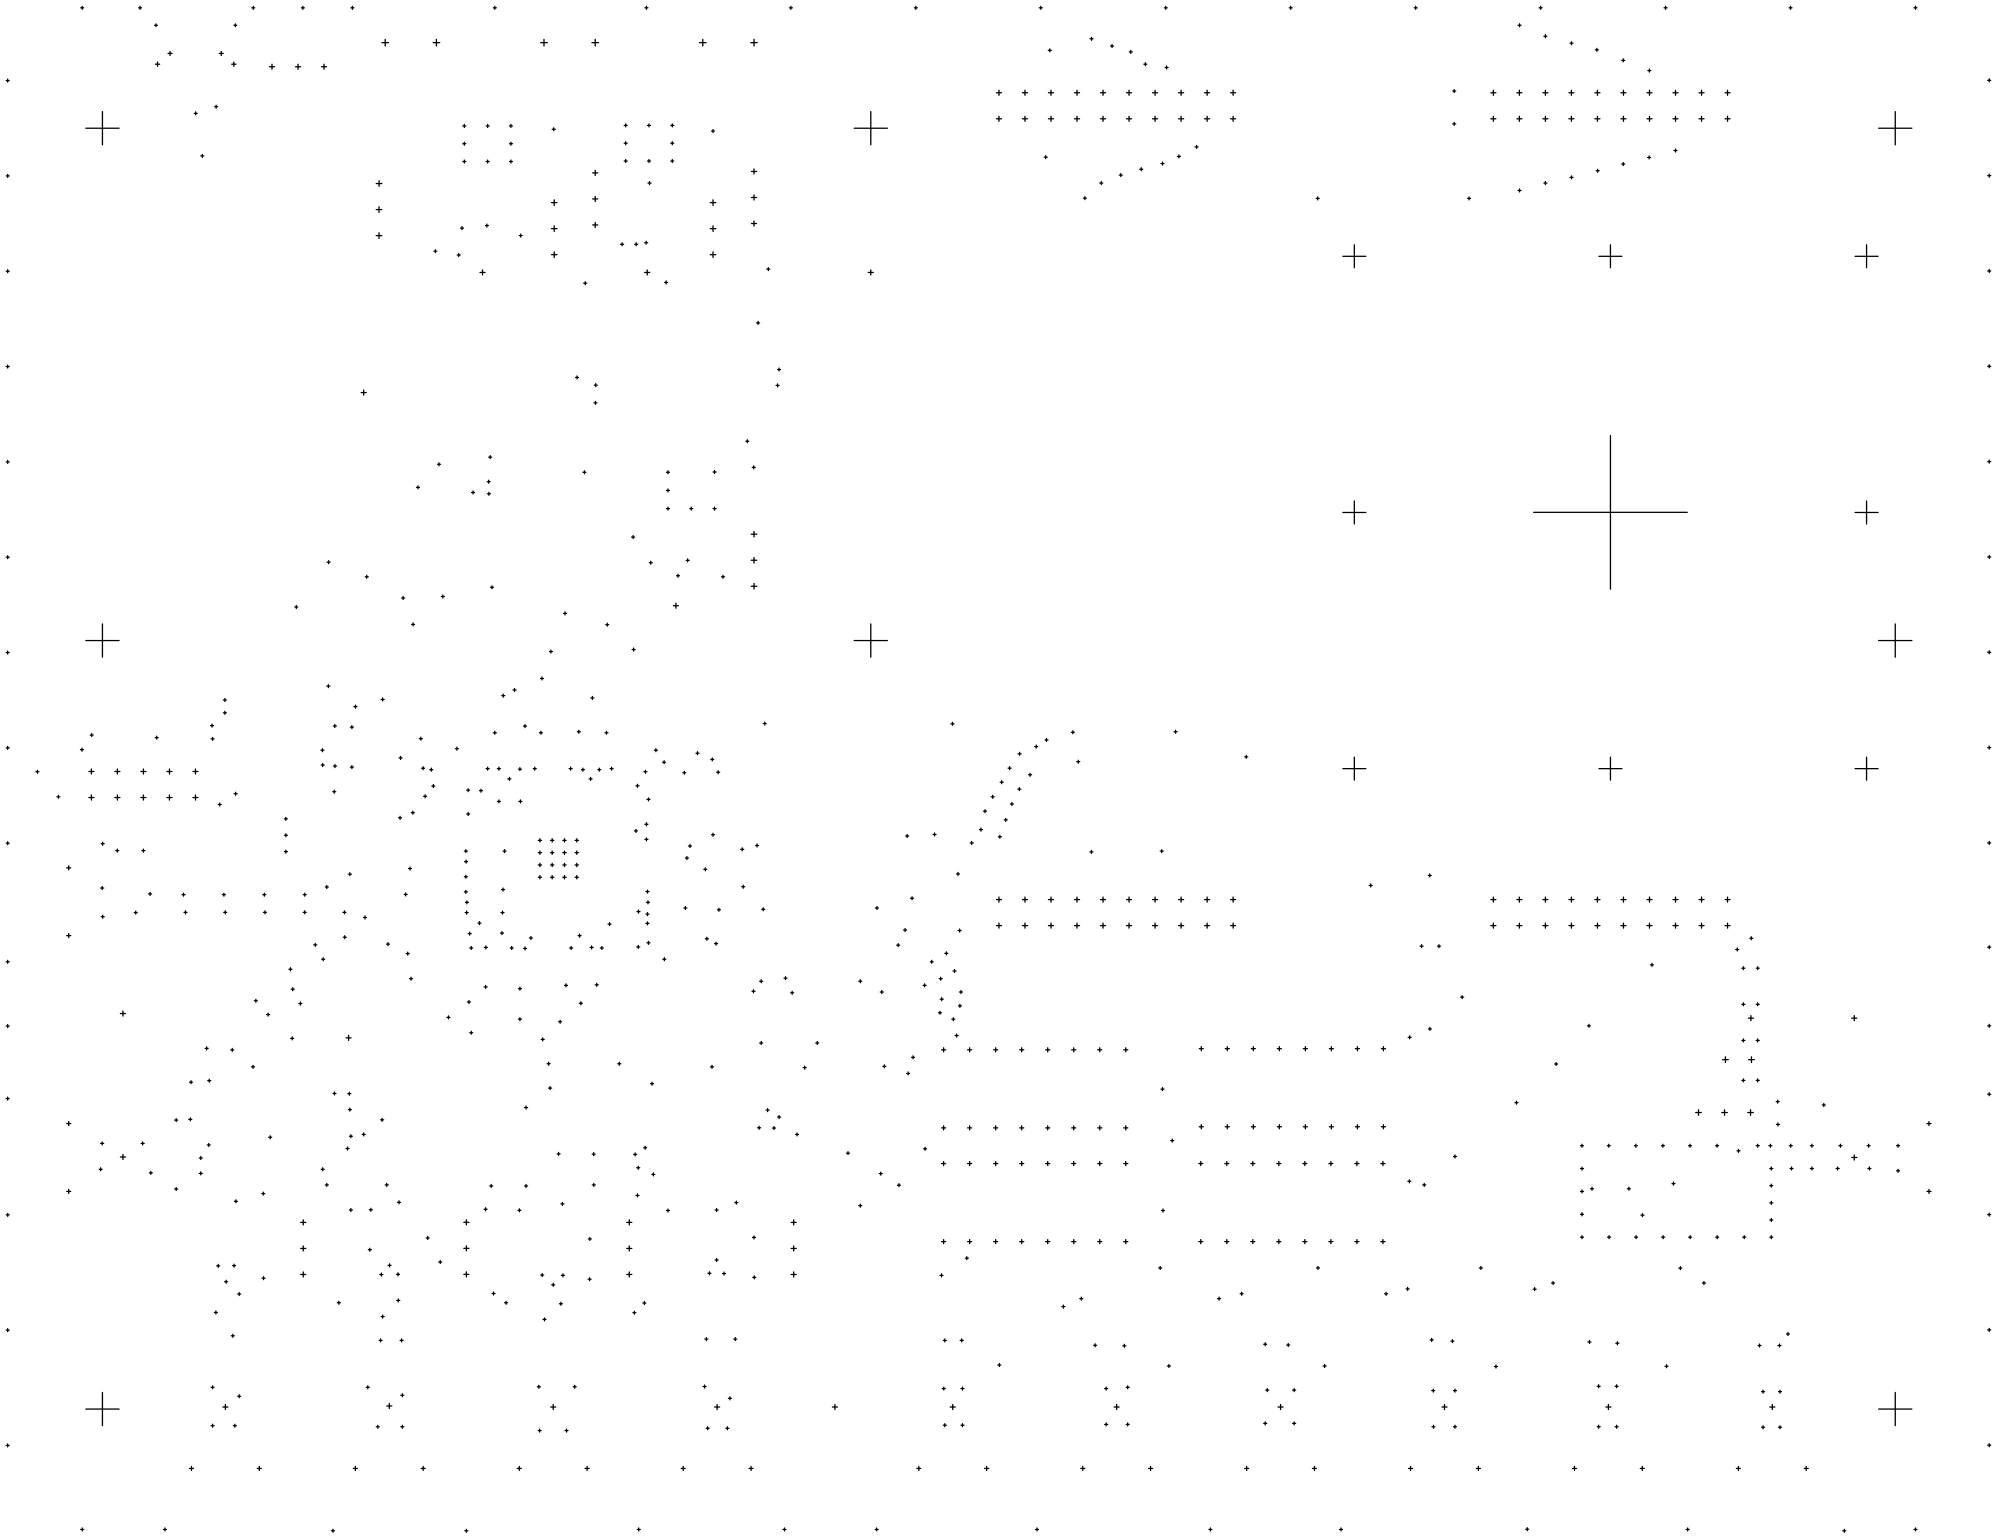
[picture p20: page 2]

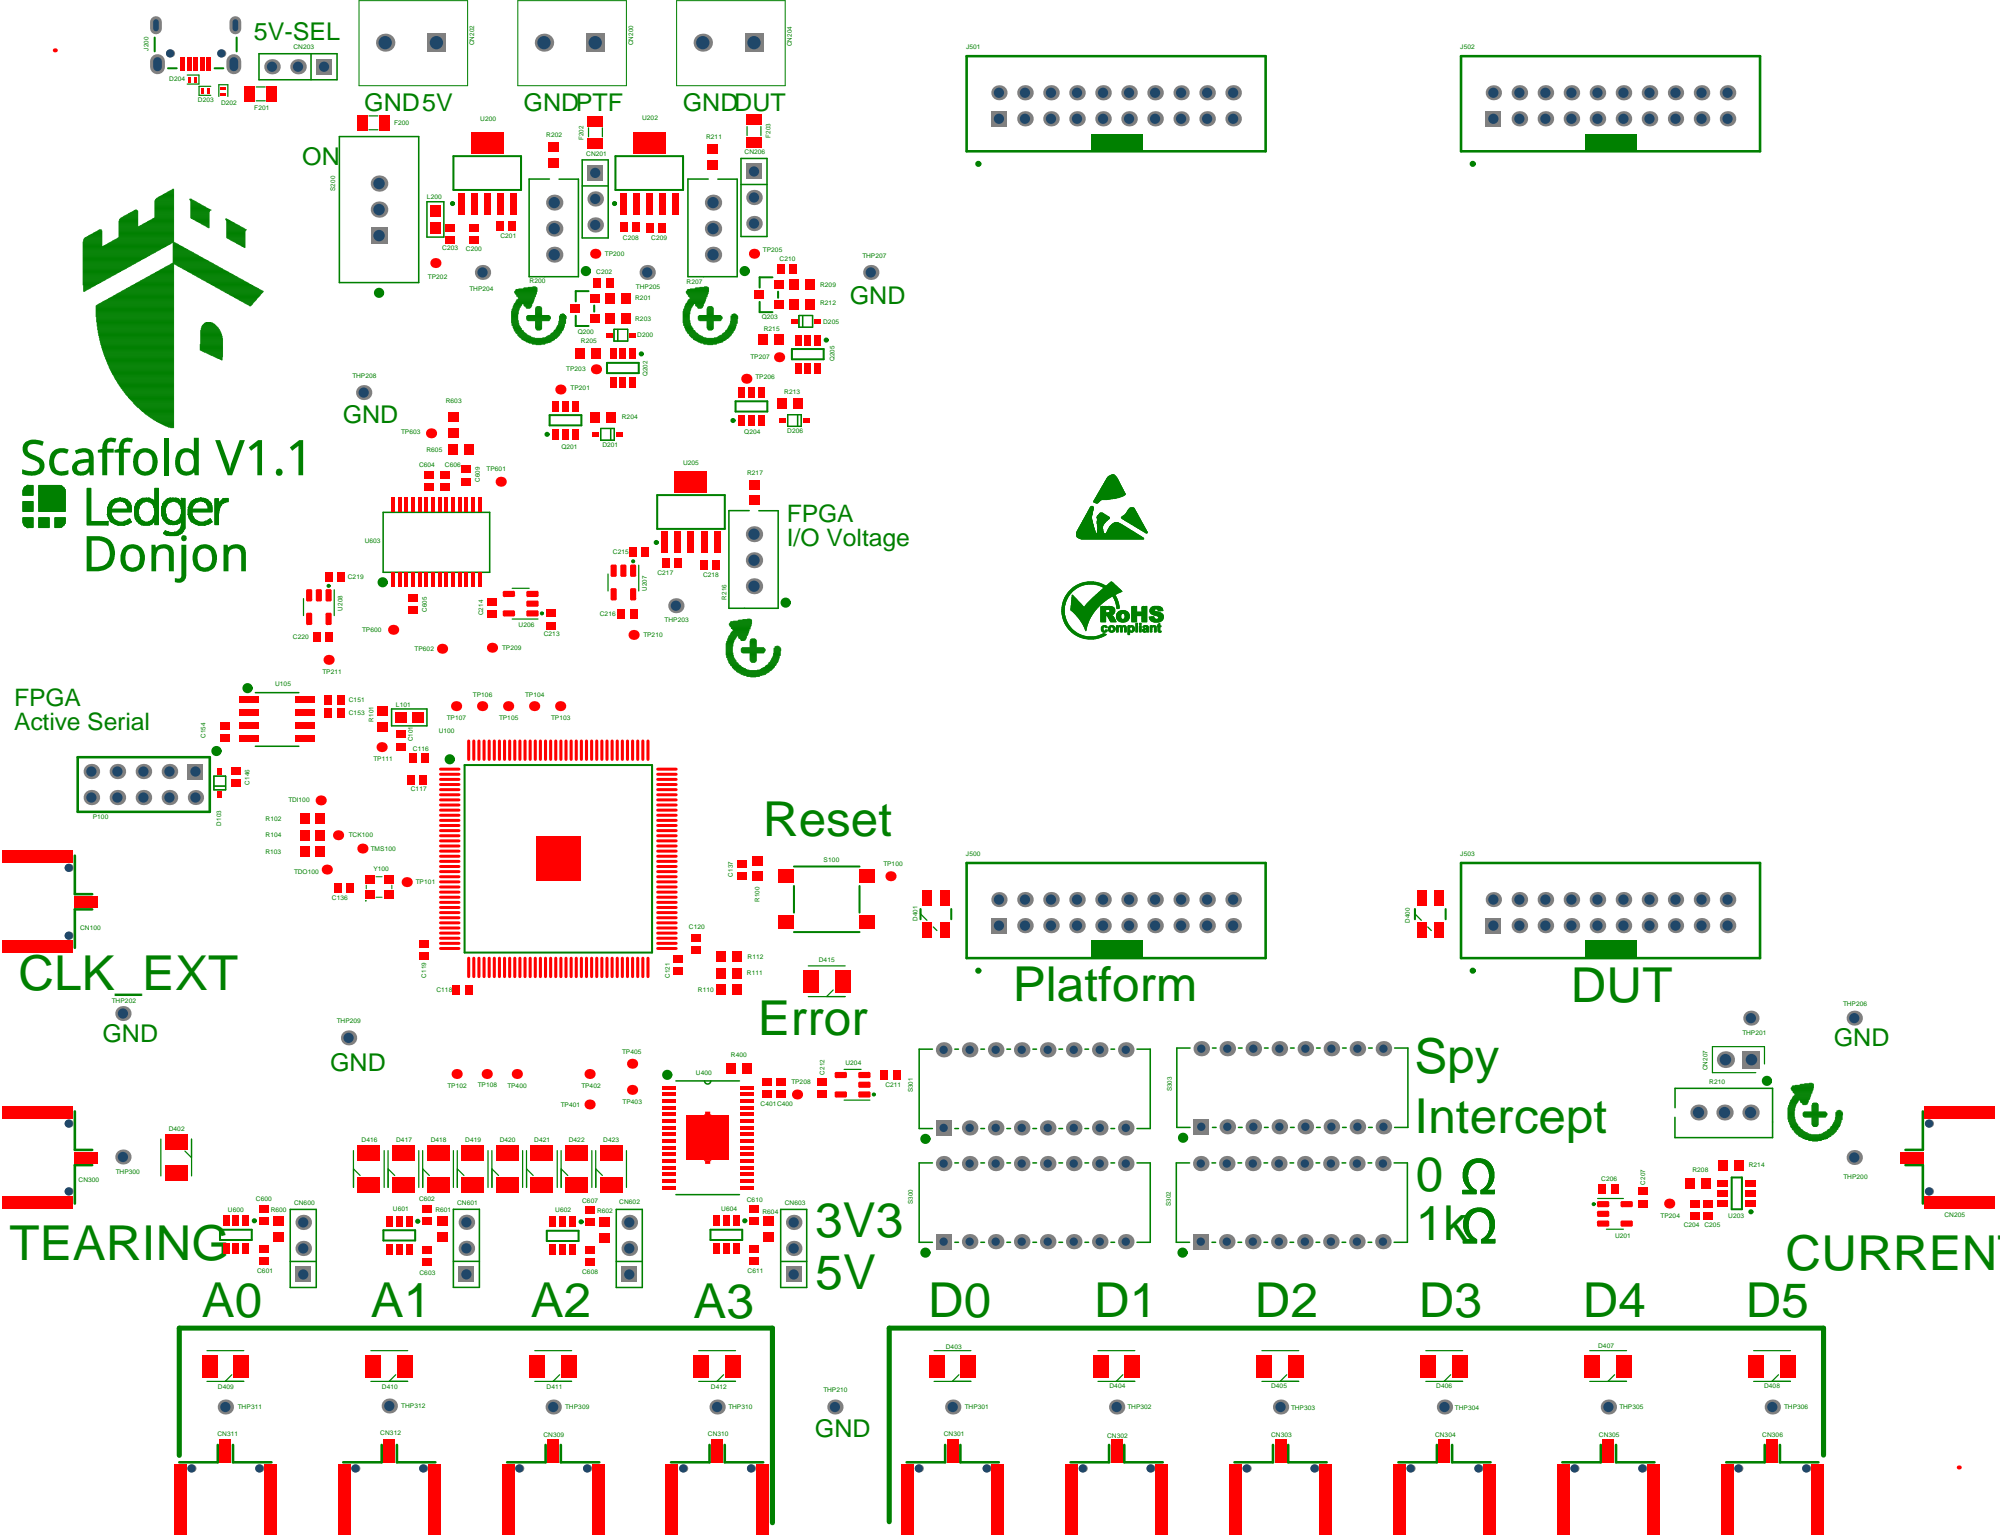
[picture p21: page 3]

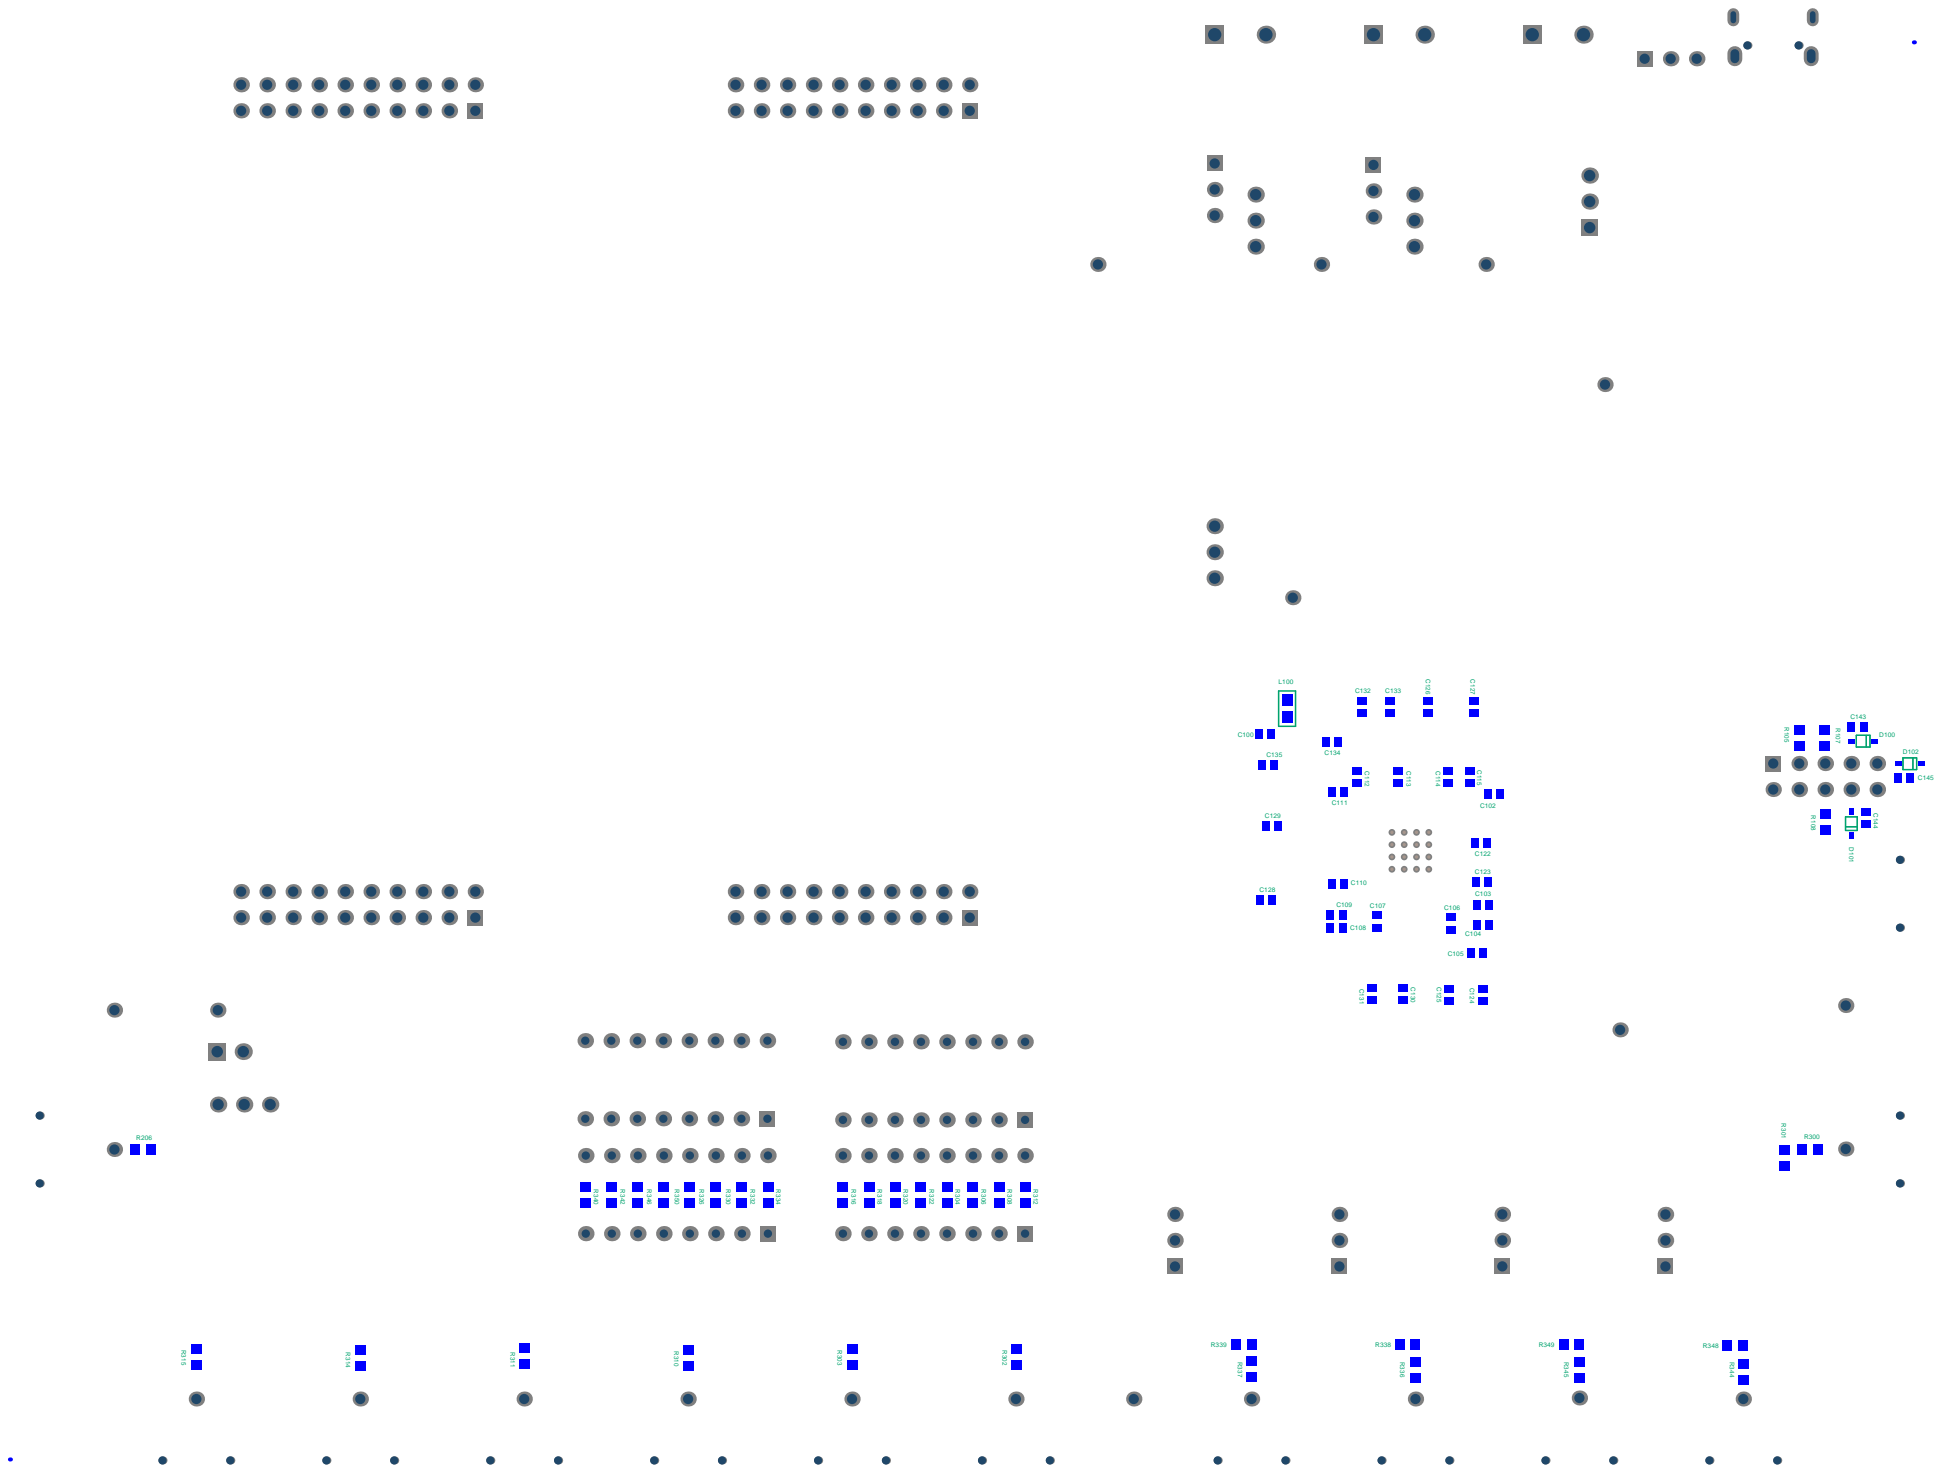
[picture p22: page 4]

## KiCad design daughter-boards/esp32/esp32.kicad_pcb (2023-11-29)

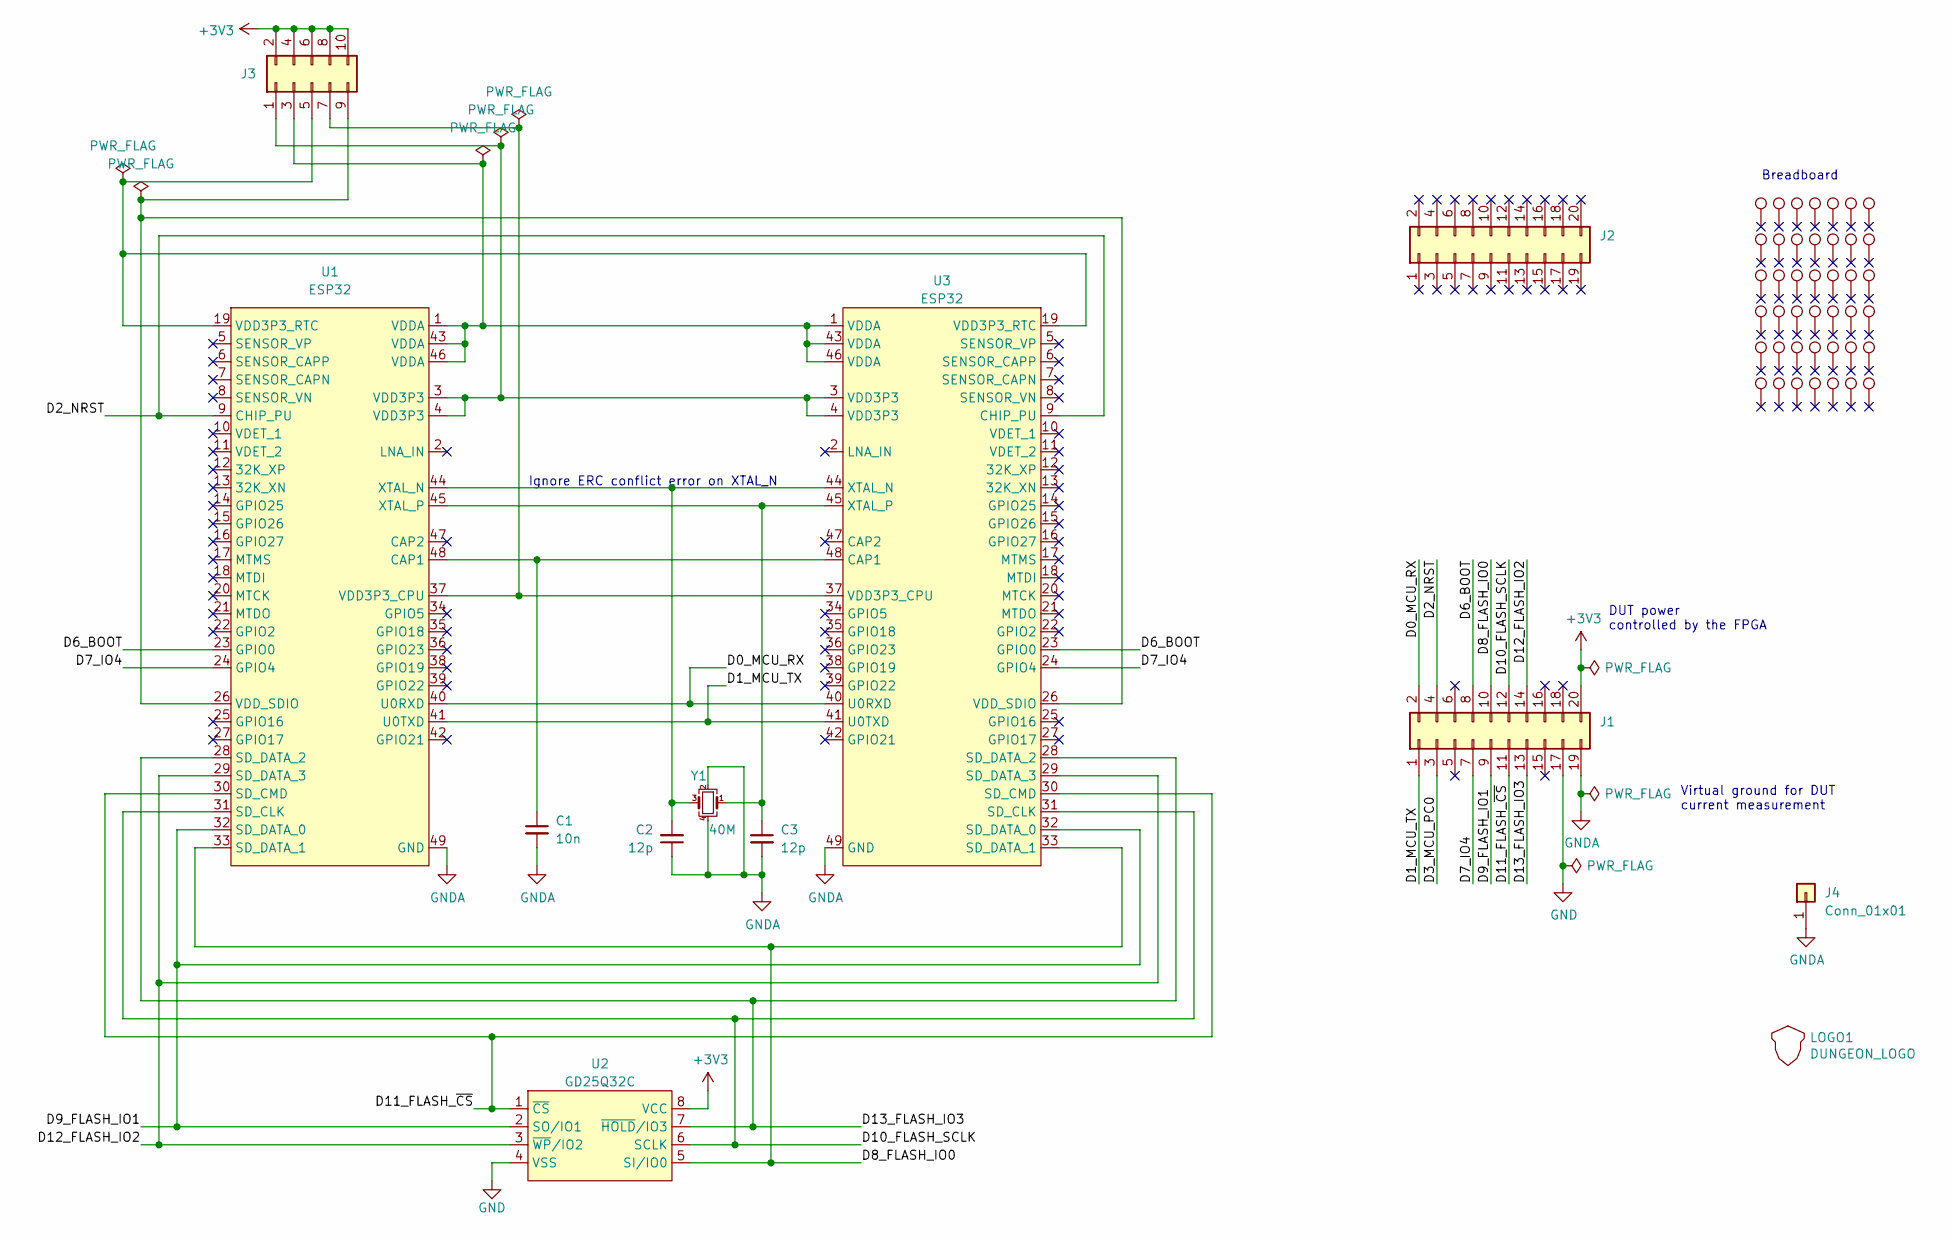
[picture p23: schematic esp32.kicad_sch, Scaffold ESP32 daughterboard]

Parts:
C1: 10n; C_0603_1608Metric
C2, C3: 12p; C_0603_1608Metric
J1, J2: Conn_02x10_Odd_Even; PinSocket_2x10_P2.54mm_Vertical
J3: Conn_02x05_Odd_Even; PinHeader_2x05_P2.54mm_Vertical
J4: Conn_01x01; PinHeader_1x01_P2.54mm_Vertical
LOGO1: DUNGEON_LOGO; donjon-2000
TP1, TP2, TP3, TP4, TP5, TP6, TP7, TP8, TP9, TP10, TP11, TP12, TP13, TP14, TP15, TP16, TP17, TP18, TP19, TP20, TP21, TP22, TP23, TP24, TP25, TP26, TP27, TP28, TP29, TP30, TP31, TP32, TP33, TP34, TP35, TP36, TP37, TP38, TP39, TP40, TP41, TP42: TestPoint; TEST_BREADBOARD_RECTANGULAR
U1, U3: ESP32; QFN-48-1EP_6x6mm_P0.4mm_EP4.3x4.3mm
U2: GD25Q32C; SOP-8_5.28x5.23mm_P1.27mm
Y1: 40M; Crystal_SMD_2520-4Pin_2.5x2.0mm

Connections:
+3V3: J1.20, J3.2, J3.4, J3.6, J3.8, J3.10, U2.8 (VCC)
/D0_MCU_RX: J1.2, U1.40 (U0RXD), U3.40 (U0RXD)
/D1_MCU_TX: J1.1, U1.41 (U0TXD), U3.41 (U0TXD)
/D2_NRST: J1.4, U1.9 (CHIP_PU), U3.9 (CHIP_PU)
/D3_MCU_PC0: J1.3
/D6_BOOT: J1.8, U1.23 (GPIO0), U3.23 (GPIO0)
/D7_IO4: J1.7, U1.24 (GPIO4), U3.24 (GPIO4)
/D8_FLASH_IO0: J1.10, U1.33 (SD_DATA_1), U2.5 (SI/IO0), U3.33 (SD_DATA_1)
/D9_FLASH_IO1: J1.9, U1.32 (SD_DATA_0), U2.2 (SO/IO1), U3.32 (SD_DATA_0)
/D10_FLASH_SCLK: J1.12, U1.31 (SD_CLK), U2.6 (SCLK), U3.31 (SD_CLK)
/D11_FLASH_~CS: J1.11, U1.30 (SD_CMD), U2.1 (~CS), U3.30 (SD_CMD)
/D12_FLASH_IO2: J1.14, U1.29 (SD_DATA_3), U2.3 (~WP~/IO2), U3.29 (SD_DATA_3)
/D13_FLASH_IO3: J1.13, U1.28 (SD_DATA_2), U2.7 (~HOLD~/IO3), U3.28 (SD_DATA_2)
GND: J1.17, U2.4 (VSS)
GNDA: C1.2, C2.1, C3.2, J1.19, J4.1, U1.49 (GND), U3.49 (GND), Y1.2, Y1.4
unnamed: C1.1, U1.48 (CAP1), U3.48 (CAP1)
unnamed: C2.2, U1.44 (XTAL_N), U3.44 (XTAL_N), Y1.3
unnamed: C3.1, U1.45 (XTAL_P), U3.45 (XTAL_P), Y1.1
unnamed: J3.1, U1.3 (VDD3P3), U1.4 (VDD3P3), U3.3 (VDD3P3), U3.4 (VDD3P3)
unnamed: J3.3, U1.1 (VDDA), U1.43 (VDDA), U1.46 (VDDA), U3.1 (VDDA), U3.43 (VDDA), U3.46 (VDDA)
unnamed: J3.5, U1.19 (VDD3P3_RTC), U3.19 (VDD3P3_RTC)
unnamed: J3.7, U1.37 (VDD3P3_CPU), U3.37 (VDD3P3_CPU)
unnamed: J3.9, U1.26 (VDD_SDIO), U3.26 (VDD_SDIO)

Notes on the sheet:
Ignore ERC conflict error on XTAL_N
DUT power controlled by the FPGA
Virtual ground for DUT current measurement
Breadboard

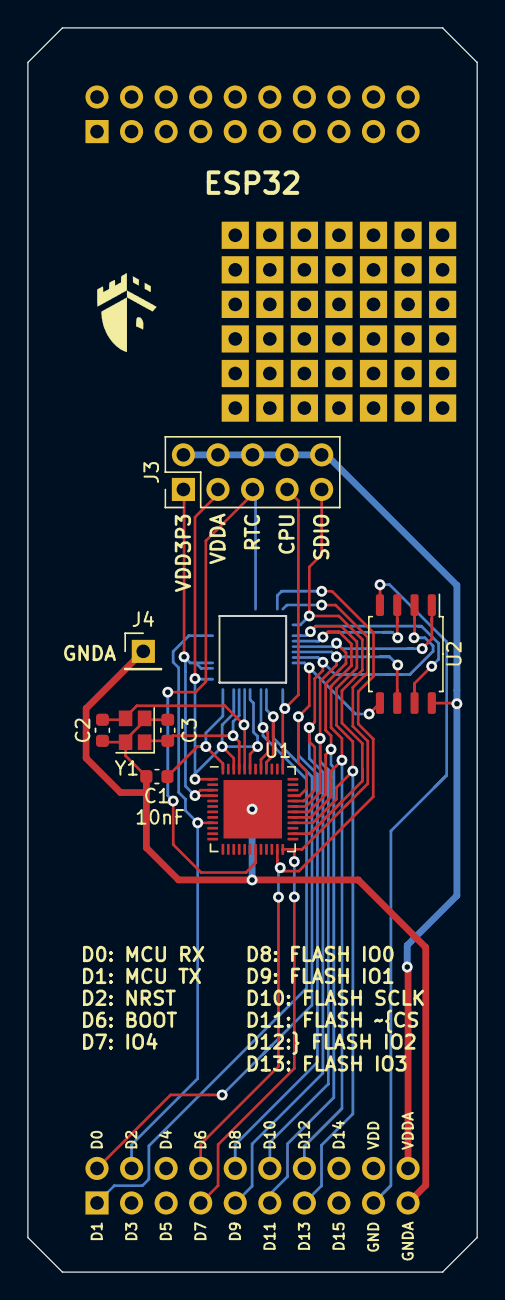
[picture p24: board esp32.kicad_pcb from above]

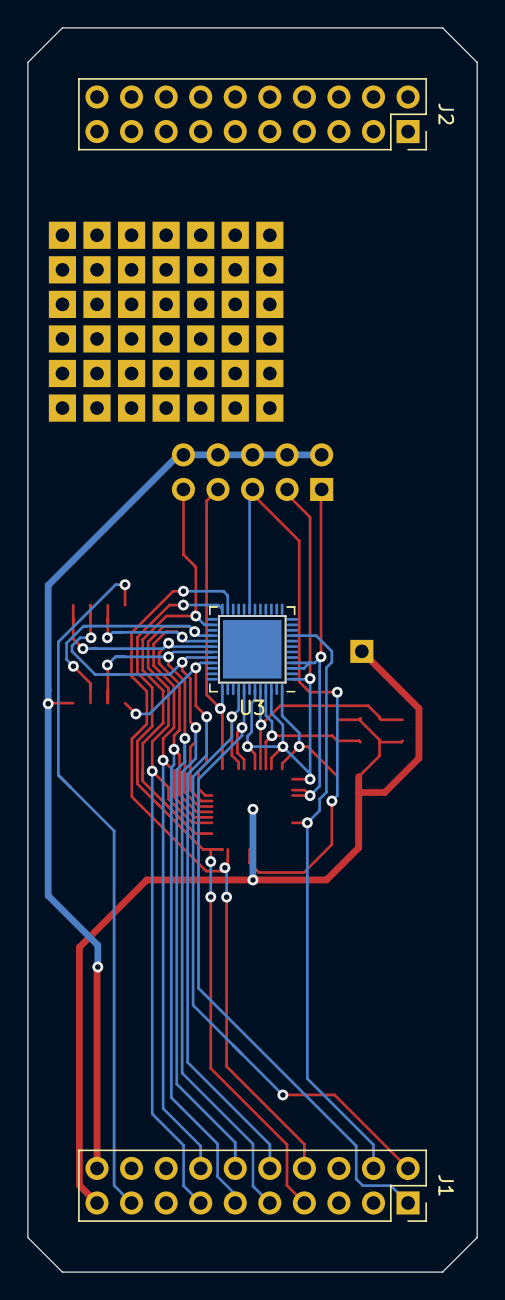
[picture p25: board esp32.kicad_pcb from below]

Board: 2 copper layers, 33.0 x 91.4 mm, 54 parts (3 on the bottom side), 22 nets.

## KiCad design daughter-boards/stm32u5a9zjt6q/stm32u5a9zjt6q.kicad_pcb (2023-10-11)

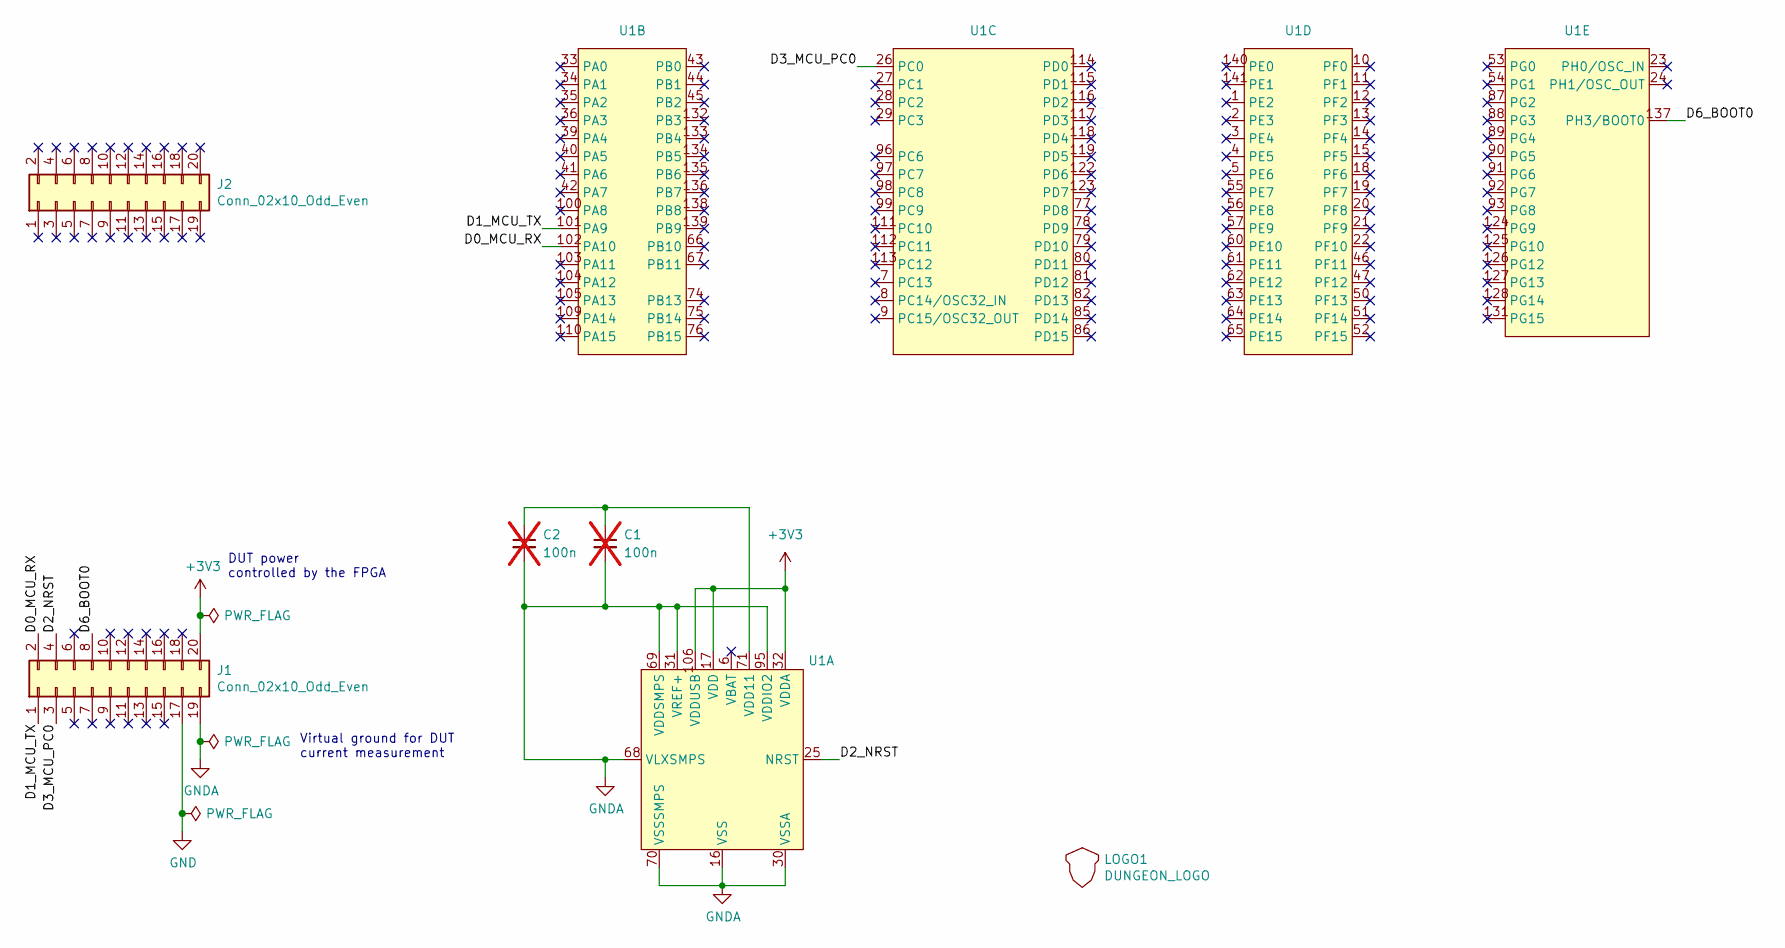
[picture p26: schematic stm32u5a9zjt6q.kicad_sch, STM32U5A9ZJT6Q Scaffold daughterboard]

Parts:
C1, C2: 100n; C_0603_1608Metric; not fitted
J1, J2: Conn_02x10_Odd_Even; PinSocket_2x10_P2.54mm_Vertical
LOGO1: DUNGEON_LOGO; donjon-2000
U1: LQFP-144_20x20mm_P0.5mm

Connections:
+3V3: J1.20, U1.17 (VDD), U1.32 (VDDA), U1.38 (VDD), U1.49 (VDD), U1.59 (VDD), U1.73 (VDD), U1.84 (VDD), U1.106 (VDDUSB), U1.108 (VDD), U1.121 (VDD), U1.144 (VDD)
/D0_MCU_RX: J1.2, U1.102 (PA10)
/D1_MCU_TX: J1.1, U1.101 (PA9)
/D2_NRST: J1.4, U1.25 (NRST)
/D3_MCU_PC0: J1.3, U1.26 (PC0)
/D6_BOOT0: J1.8, U1.137 (PH3/BOOT0)
GND: J1.17
GNDA: C1.2, C2.2, J1.19, U1.16 (VSS), U1.30 (VSSA), U1.31 (VREF+), U1.37 (VSS), U1.48 (VSS), U1.58 (VSS), U1.68 (VLXSMPS), U1.69 (VDDSMPS), U1.70 (VSSSMPS), U1.72 (VSS), U1.83 (VSS), U1.94 (VSS), U1.95 (VDDIO2), U1.107 (VSS), U1.120 (VSS), U1.129 (VSS), U1.130 (VDDIO2), U1.143 (VSS)
unnamed: C1.1, C2.1, U1.71 (VDD11), U1.142 (VDD11)

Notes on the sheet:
Virtual ground for DUT current measurement
DUT power controlled by the FPGA

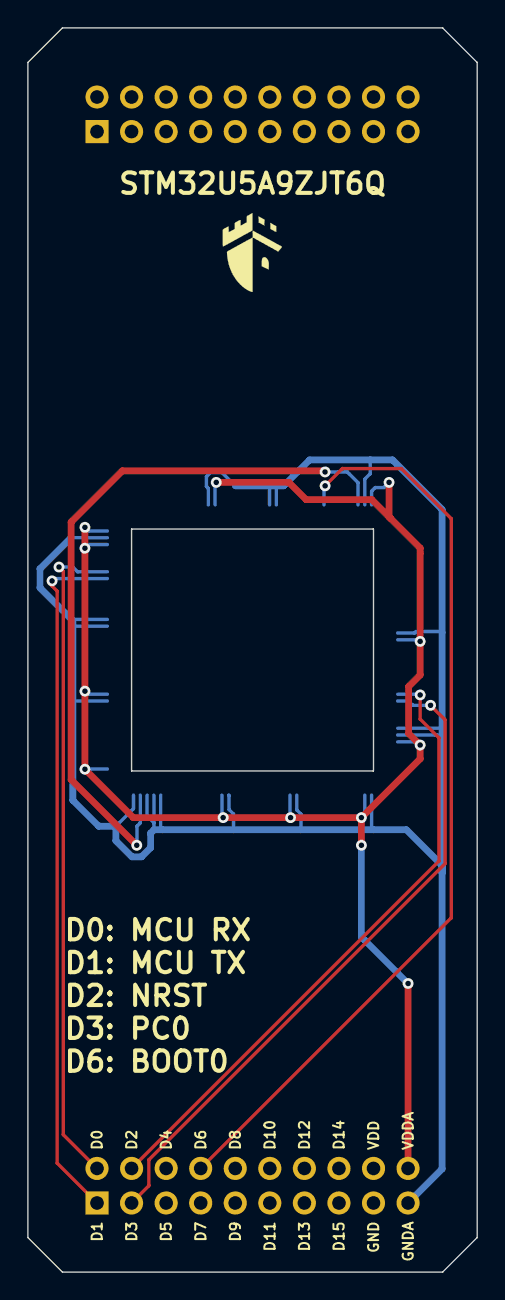
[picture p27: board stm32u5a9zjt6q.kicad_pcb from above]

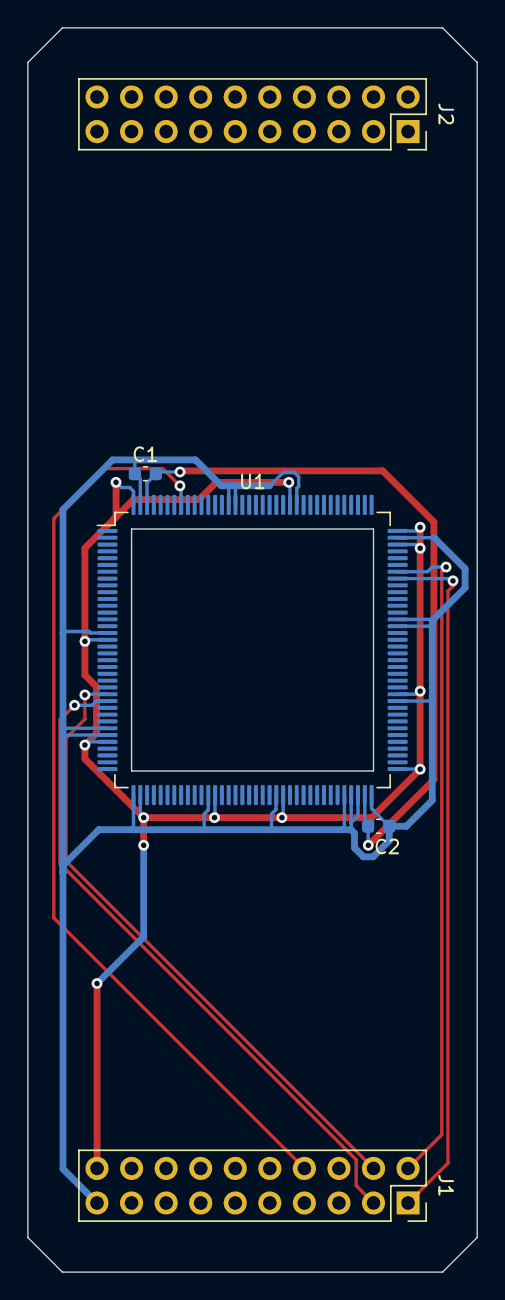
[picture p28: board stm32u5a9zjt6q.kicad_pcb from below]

Board: 2 copper layers, 33.0 x 91.4 mm, 6 parts (5 on the bottom side), 8 nets.

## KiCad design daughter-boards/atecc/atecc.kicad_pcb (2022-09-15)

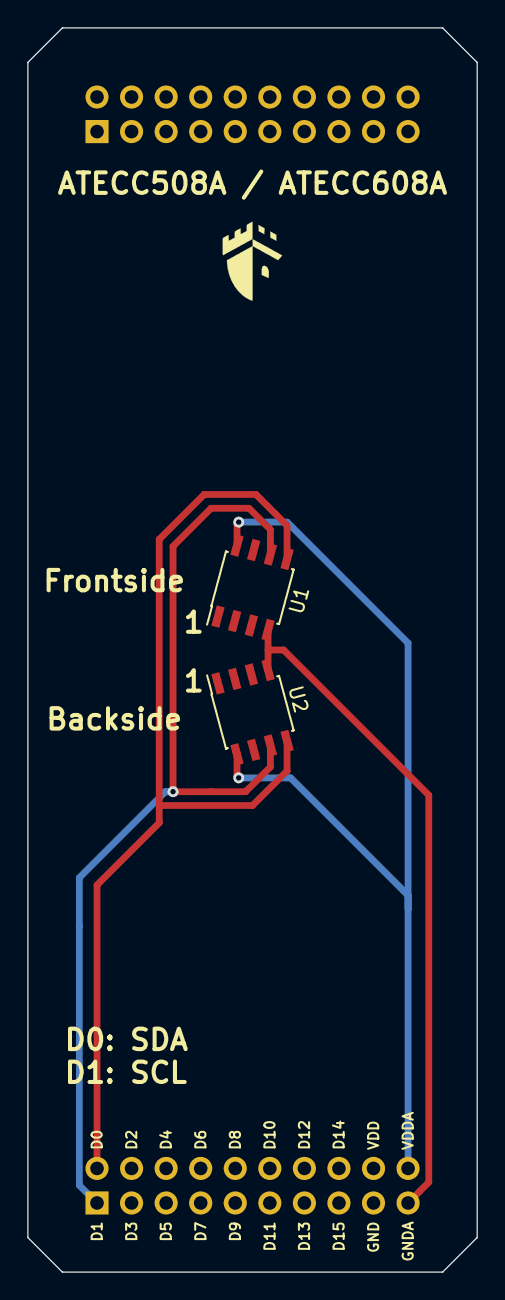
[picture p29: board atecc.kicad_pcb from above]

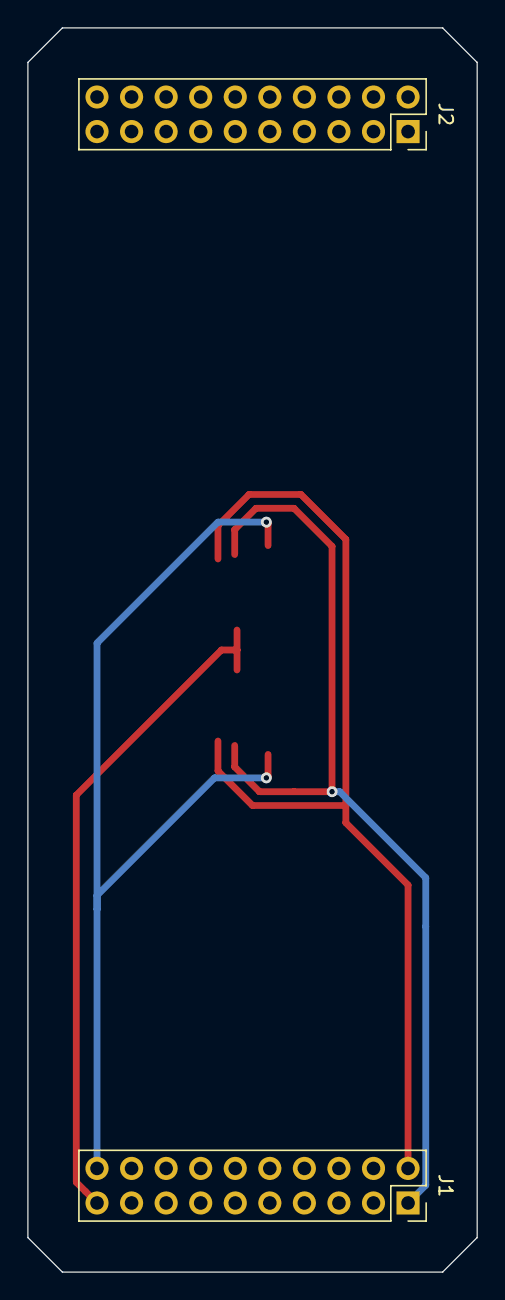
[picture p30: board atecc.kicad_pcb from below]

Board: 2 copper layers, 33.0 x 91.4 mm, 5 parts (2 on the bottom side), 4 nets.

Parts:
J1, J2: Conn_02x10_Odd_Even; PinSocket_2x10_P2.54mm_Vertical
LOGO1: DUNGEON_LOGO; donjon-2000
U1: ATECC508A; SOIC-8_3.9x4.9mm_P1.27mm
U2: ATECC508A; FLIP-SOIC-8_3.9x4.9mm_P1.27mm

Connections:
/D0: J1.2, U1.5, U2.5
/D1: J1.1, U1.6, U2.6
GNDA: J1.19, U1.4, U2.4
VDDA: J1.20, U1.8, U2.8

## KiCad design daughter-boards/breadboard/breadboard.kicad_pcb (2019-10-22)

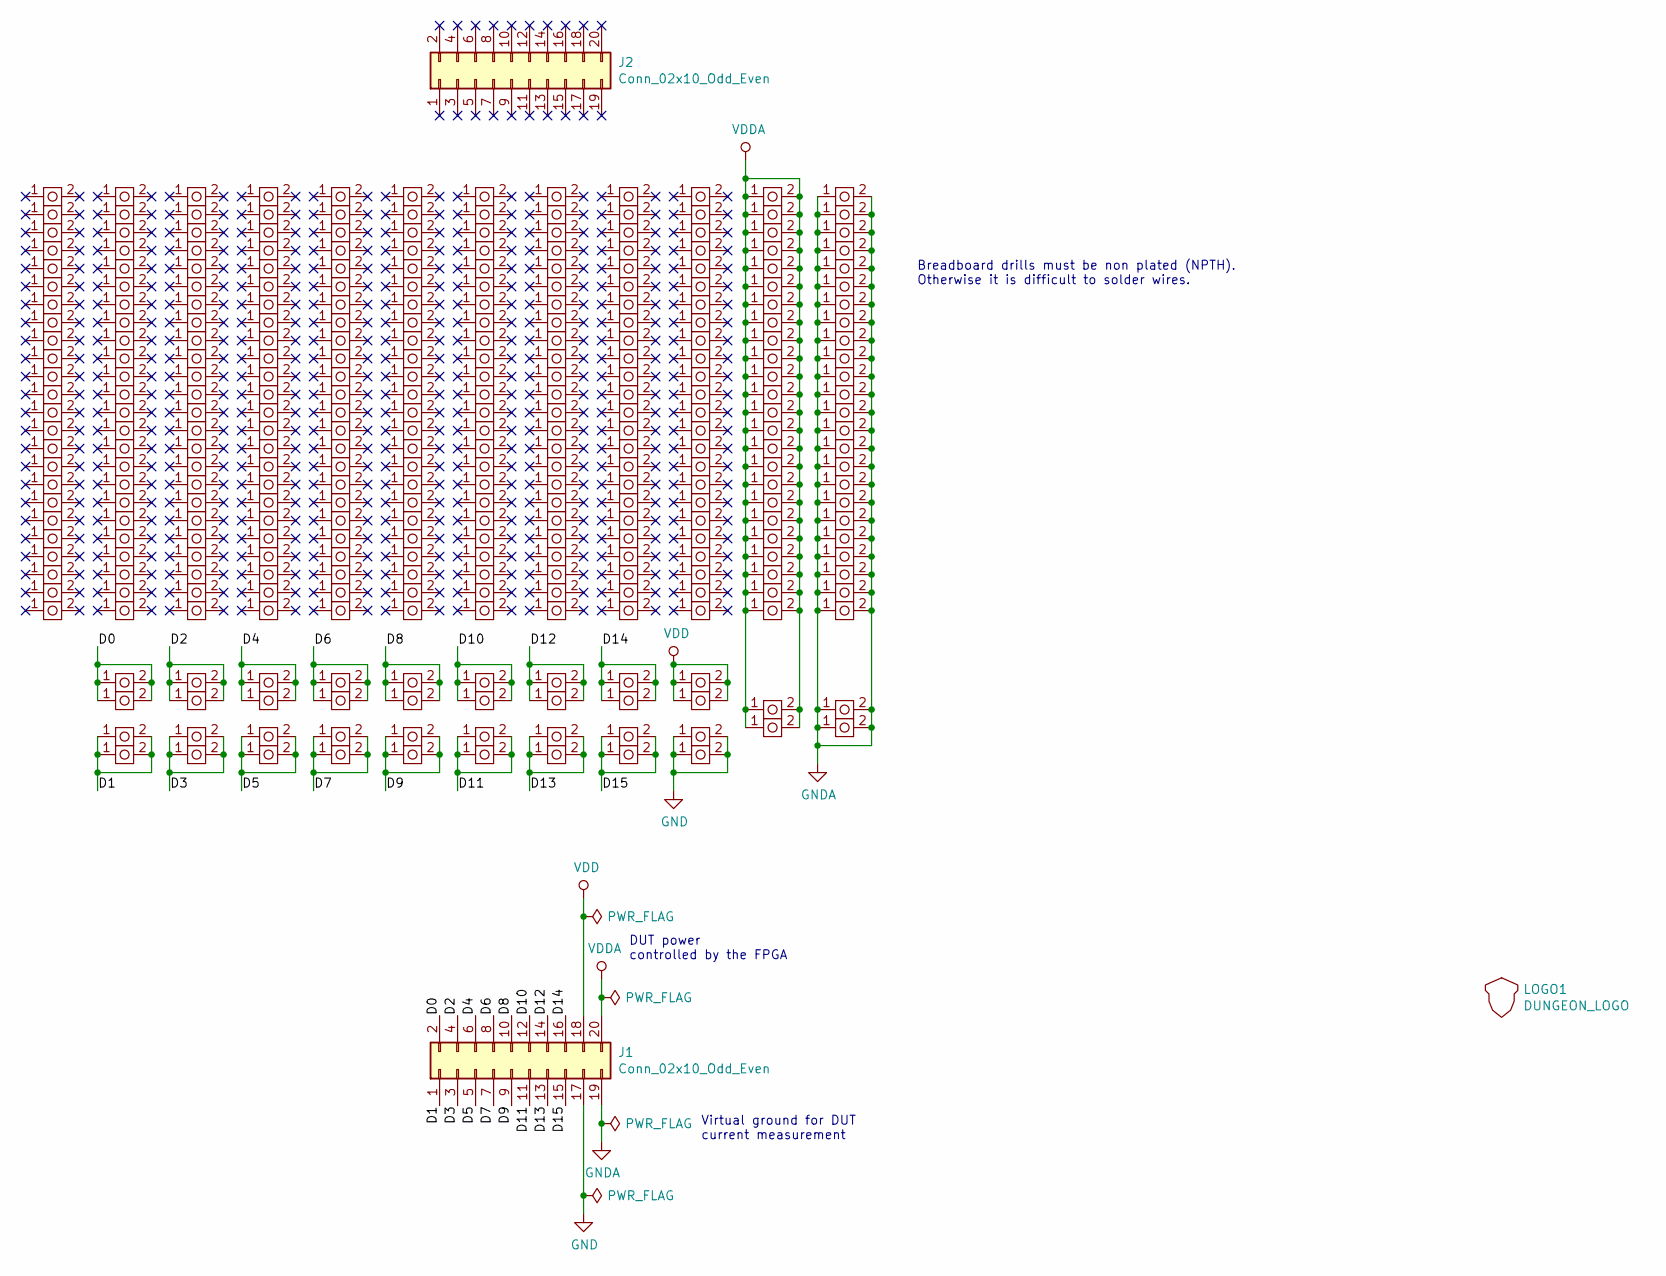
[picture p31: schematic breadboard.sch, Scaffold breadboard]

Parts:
J1, J2: Conn_02x10_Odd_Even; PinSocket_2x10_P2.54mm_Vertical
LOGO1: DUNGEON_LOGO; donjon-3000
U1, U2, U3, U4, U5, U6, U7, U8, U9, U10, U11, U12, U13, U14, U15, U16, U17, U18, U19, U20, U21, U22, U23, U24, U25, U26, U27, U28, U29, U30, U31, U32, U33, U34, U35, U36, U37, U38, U39, U40, U41, U42, U43, U44, U45, U46, U47, U48, U49, U50, U51, U52, U53, U54, U55, U56, U57, U58, U59, U60, U61, U62, U63, U64, U65, U66, U67, U68, U69, U70, U71, U72, U73, U74, U75, U76, U77, U78, U79, U80, U81, U82, U83, U84, U85, U86, U87, U88, U89, U90, U91, U92, U93, U94, U95, U96, U97, U98, U99, U100, U101, U102, U103, U104, U105, U106, U107, U108, U109, U110, U111, U112, U113, U114, U115, U116, U117, U118, U119, U120, U121, U122, U123, U124, U125, U126, U127, U128, U129, U130, U131, U132, U133, U134, U135, U136, U137, U138, U139, U140, U141, U142, U143, U144, U145, U146, U147, U148, U149, U150, U151, U152, U153, U154, U155, U156, U157, U158, U159, U160, U161, U162, U163, U164, U165, U166, U167, U168, U169, U170, U171, U172, U173, U174, U175, U176, U177, U178, U179, U180, U181, U182, U183, U184, U185, U186, U187, U188, U189, U190, U191, U192, U193, U194, U195, U196, U197, U198, U199, U200, U201, U202, U203, U204, U205, U206, U207, U208, U209, U210, U211, U212, U213, U214, U215, U216, U217, U218, U219, U220, U221, U222, U223, U224, U225, U226, U227, U228, U229, U230, U231, U232, U233, U234, U235, U236, U237, U238, U239, U240, U241, U242, U243, U244, U245, U246, U247, U248, U249, U250, U251, U252, U253, U254, U255, U256, U257, U258, U259, U260, U261, U262, U263, U264, U265, U266, U267, U268, U269, U270, U271, U272, U273, U274, U275, U276, U277, U278, U279, U280, U281, U282, U283, U284, U285, U286, U287, U288, U289, U290, U291, U292, U293, U294, U295, U296, U297, U298, U299, U300, U301, U302, U303, U304, U305, U306, U307, U308, U309, U310, U311, U312, U313, U314, U315, U316, U317, U318, U319, U320, U321, U322, U323, U324, U325, U326, U327, U328: BREADBOARD_NPTH; TEST_BREADBOARD_RECTANGULAR_NPTH2

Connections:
/D0: J1.2, U297.1, U297.2, U298.1, U298.2
/D1: J1.1, U299.1, U299.2, U300.1, U300.2
/D2: J1.4, U301.1, U301.2, U302.1, U302.2
/D3: J1.3, U303.1, U303.2, U304.1, U304.2
/D4: J1.6, U305.1, U305.2, U306.1, U306.2
/D5: J1.5, U307.1, U307.2, U308.1, U308.2
/D6: J1.8, U309.1, U309.2, U310.1, U310.2
/D7: J1.7, U311.1, U311.2, U312.1, U312.2
/D8: J1.10, U313.1, U313.2, U314.1, U314.2
/D9: J1.9, U315.1, U315.2, U316.1, U316.2
/D10: J1.12, U317.1, U317.2, U318.1, U318.2
/D11: J1.11, U319.1, U319.2, U320.1, U320.2
/D12: J1.14, U321.1, U321.2, U322.1, U322.2
/D13: J1.13, U323.1, U323.2, U324.1, U324.2
/D14: J1.16, U325.1, U325.2, U326.1, U326.2
/D15: J1.15, U327.1, U327.2, U328.1, U328.2
GND: J1.17, U295.1, U295.2, U296.1, U296.2
GNDA: J1.19, U267.1, U267.2, U268.1, U268.2, U269.1, U269.2, U270.1, U270.2, U271.1, U271.2, U272.1, U272.2, U273.1, U273.2, U274.1, U274.2, U275.1, U275.2, U276.1, U276.2, U277.1, U277.2, U278.1, U278.2, U279.1, U279.2, U280.1, U280.2, U281.1, U281.2, U282.1, U282.2, U283.1, U283.2, U284.1, U284.2, U285.1, U285.2, U286.1, U286.2, U287.1, U287.2, U288.1, U288.2, U289.1, U289.2, U290.1, U290.2, U291.1, U291.2, U292.1, U292.2
VDD: J1.18, U293.1, U293.2, U294.1, U294.2
VDDA: J1.20, U241.1, U241.2, U242.1, U242.2, U243.1, U243.2, U244.1, U244.2, U245.1, U245.2, U246.1, U246.2, U247.1, U247.2, U248.1, U248.2, U249.1, U249.2, U250.1, U250.2, U251.1, U251.2, U252.1, U252.2, U253.1, U253.2, U254.1, U254.2, U255.1, U255.2, U256.1, U256.2, U257.1, U257.2, U258.1, U258.2, U259.1, U259.2, U260.1, U260.2, U261.1, U261.2, U262.1, U262.2, U263.1, U263.2, U264.1, U264.2, U265.1, U265.2, U266.1, U266.2

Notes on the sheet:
Virtual ground for DUT current measurement
DUT power controlled by the FPGA
Breadboard drills must be non plated (NPTH). Otherwise it is difficult to solder wires.

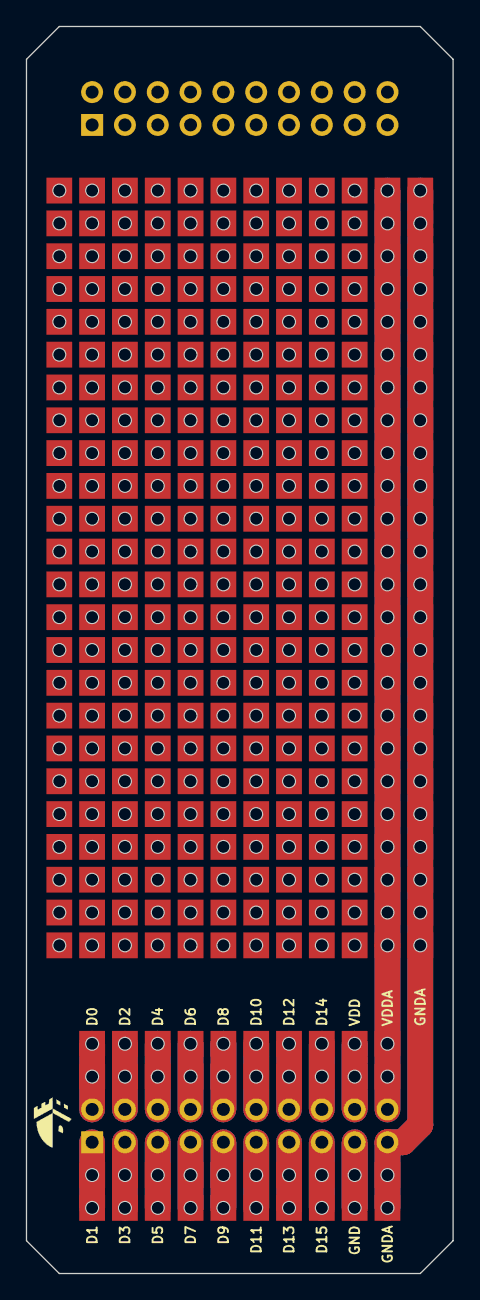
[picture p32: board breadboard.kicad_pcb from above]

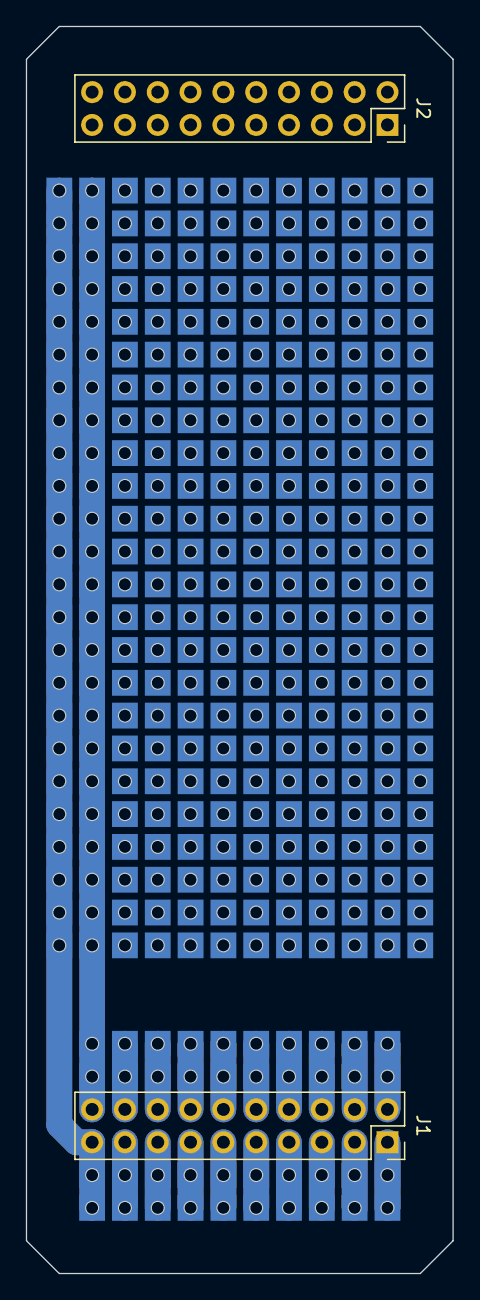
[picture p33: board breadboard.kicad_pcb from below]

Board: 2 copper layers, 33.0 x 96.5 mm, 331 parts (2 on the bottom side), 20 nets.

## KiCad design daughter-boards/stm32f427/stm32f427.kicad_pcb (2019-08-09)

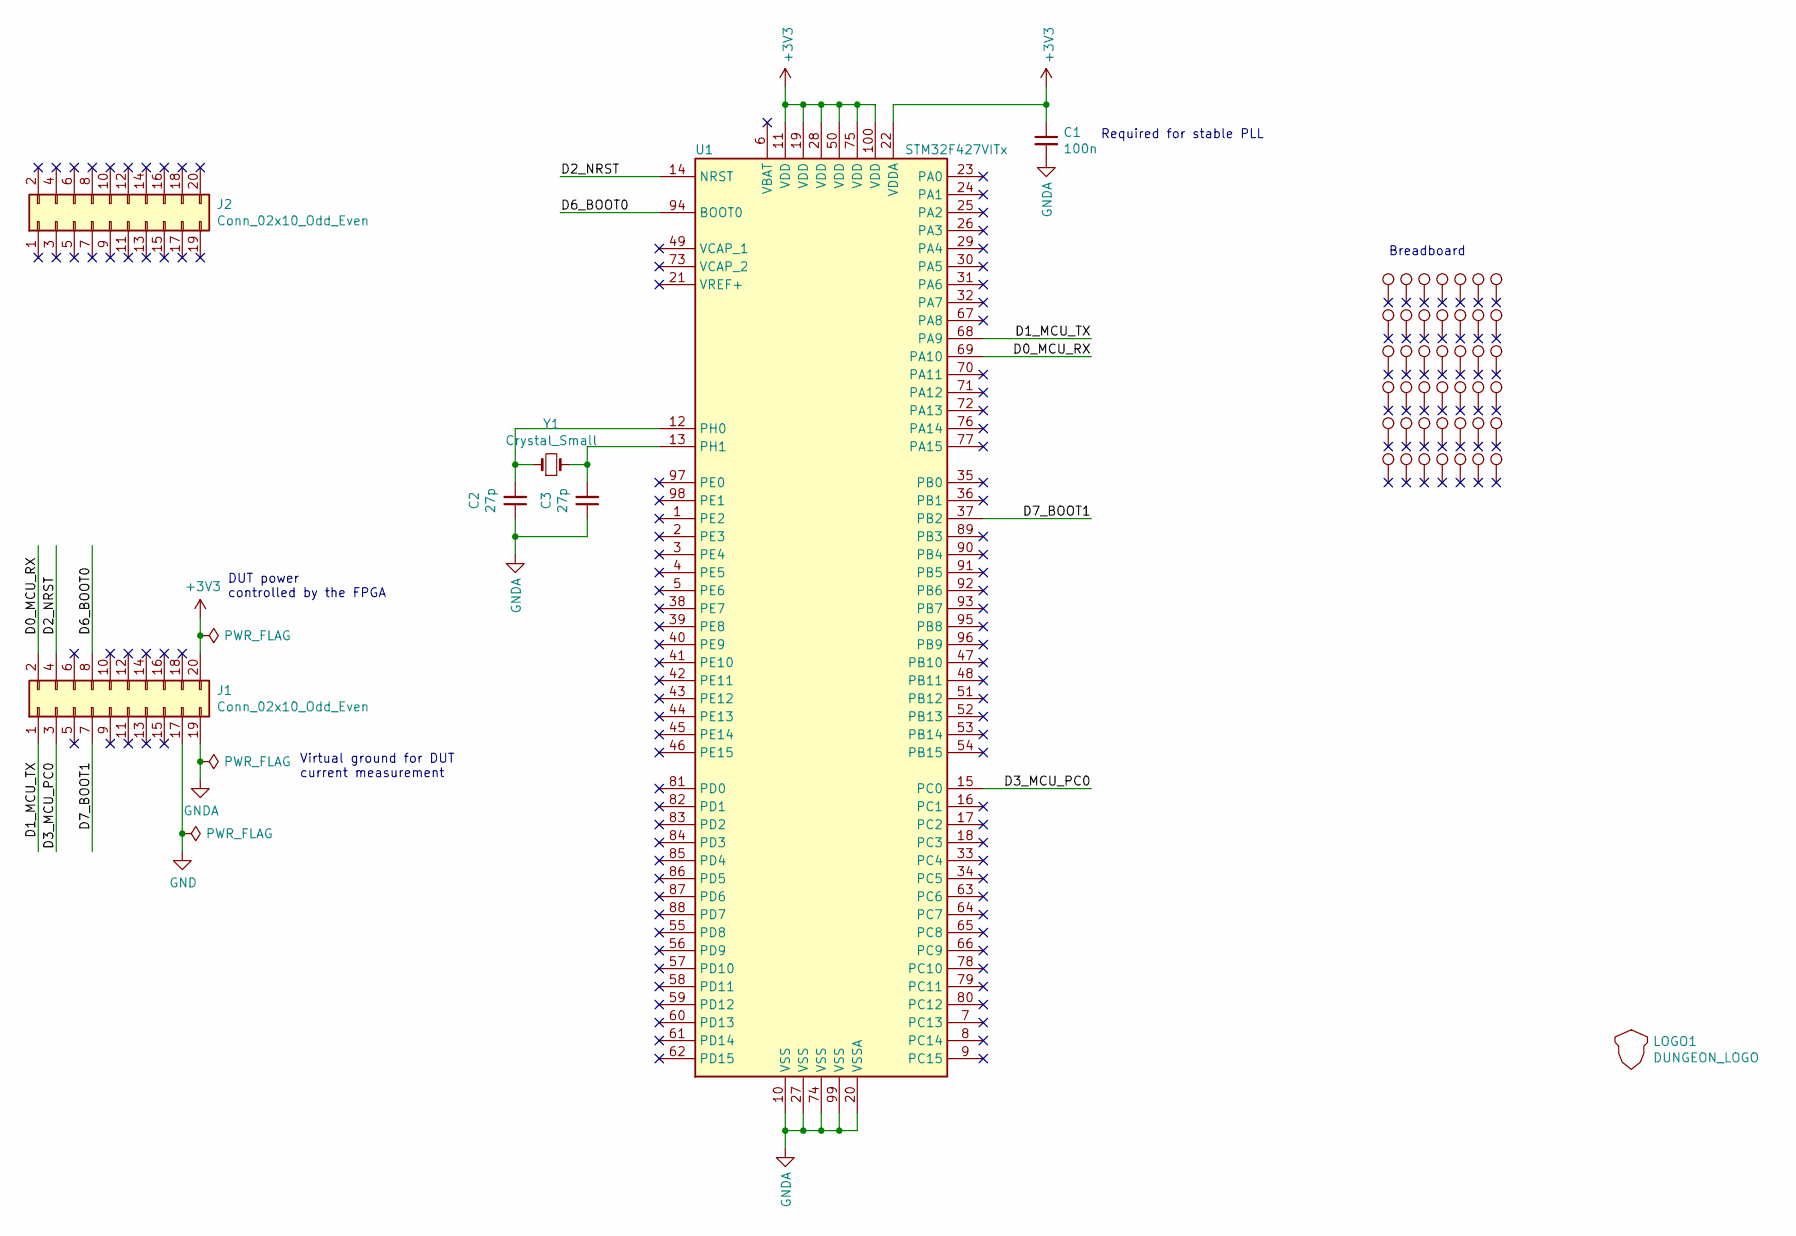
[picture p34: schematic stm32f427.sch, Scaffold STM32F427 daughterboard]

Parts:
C1: 100n; C_0805_2012Metric
C2, C3: 27p; C_0805_2012Metric
J1, J2: Conn_02x10_Odd_Even; PinSocket_2x10_P2.54mm_Vertical
LOGO1: DUNGEON_LOGO; donjon-2000
TP1, TP2, TP3, TP4, TP5, TP6, TP7, TP8, TP9, TP10, TP11, TP12, TP13, TP14, TP15, TP16, TP17, TP18, TP19, TP20, TP21, TP22, TP23, TP24, TP25, TP26, TP27, TP28, TP29, TP30, TP31, TP32, TP33, TP34, TP35, TP36, TP37, TP38, TP39, TP40, TP41, TP42: TestPoint; TEST_BREADBOARD_RECTANGULAR
U1: STM32F427VITx; ALLSOCKET-QFP100
Y1: Crystal_Small; Crystal_HC18-U_Vertical

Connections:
+3V3: C1.1, J1.20, U1.11 (VDD), U1.19 (VDD), U1.22 (VDDA), U1.28 (VDD), U1.50 (VDD), U1.75 (VDD), U1.100 (VDD)
/D0_MCU_RX: J1.2, U1.69 (PA10)
/D1_MCU_TX: J1.1, U1.68 (PA9)
/D2_NRST: J1.4, U1.14 (NRST)
/D3_MCU_PC0: J1.3, U1.15 (PC0)
/D6_BOOT0: J1.8, U1.94 (BOOT0)
/D7_BOOT1: J1.7, U1.37 (PB2)
GND: J1.17
GNDA: C1.2, C2.1, C3.1, J1.19, U1.10 (VSS), U1.20 (VSSA), U1.27 (VSS), U1.74 (VSS), U1.99 (VSS)
unnamed: C2.2, U1.12 (PH0), Y1.1
unnamed: C3.2, U1.13 (PH1), Y1.2

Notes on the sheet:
Virtual ground for DUT current measurement
DUT power controlled by the FPGA
Required for stable PLL
Breadboard



Board: 2 copper layers, 33.0 x 91.4 mm, 50 parts (5 on the bottom side), 10 nets.

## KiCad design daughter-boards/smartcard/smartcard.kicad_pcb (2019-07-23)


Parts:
J1, J2: Conn_02x10_Odd_Even; PinSocket_2x10_P2.54mm_Vertical
LOGO1: DUNGEON_LOGO; donjon-2000
R1: 100K; R_0603_1608Metric
R2: 10K; R_0603_1608Metric
TP18, TP19, TP20, TP21, TP33: TestPoint; TestPoint_Pad_D1.5mm
U1: 7334L2622F04LF; AMPHENOL_SMARTCARD_7334L2622F04LF

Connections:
/D0_IO: J1.2, R2.1, TP21.1, U1.7 (IO)
/D1_~RST~: J1.1, TP19.1, U1.2 (RST)
/D2_CLK: J1.4, TP20.1, U1.3 (CLK)
/D3_SENSE: J1.3, R1.2, U1.9
GND: J1.17, U1.10
GNDA: J1.19, TP18.1, U1.5 (GND)
VDD: J1.18, R1.1
VDDA: J1.20, R2.2, TP33.1, U1.1 (VCC)

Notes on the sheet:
Virtual ground for DUT current measurement
DUT power controlled by the FPGA
Contact open when card is inserted
Scaffold GND, don't connect to DUT
Always enabled VDD

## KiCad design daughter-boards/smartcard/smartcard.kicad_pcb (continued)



Board: 2 copper layers, 41.1 x 91.4 mm, 11 parts (4 on the bottom side), 8 nets.

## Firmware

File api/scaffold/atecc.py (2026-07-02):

# This file is part of Scaffold
#
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
#
# Copyright 2023 Ledger SAS, written by Michael Mouchous

from time import sleep
from enum import Enum, auto
from binascii import hexlify
from . import Pull, IOMode, Scaffold, I2CTrigger
from typing import Literal, Optional, Union, cast
import crcmod
from Crypto.Hash import SHA256


base_crc16 = crcmod.mkCrcFun(0x18005, 0, rev=True)


def crc16(data: bytes) -> int:
    x = base_crc16(data)
    rev = int(f"{x:016b}"[::-1], 2)
    result = ((rev & 0xFF) << 8) + (rev >> 8)
    return result


def crc16b(data: bytes) -> bytes:
    return int.to_bytes(crc16(data), 2, "big")


def swi_bits(byte: int) -> bytearray:
    result = bytearray()
    for i in range(8):
        result.append(0b11111101 + (((byte >> i) & 1) << 1))
    return result


class CRCError(Exception):
    def __init__(self, data, expected, received):
        self.data = data
        self.expected = expected
        self.received = received

    def __str__(self):
        return "CRCError"


class ProtocolError(Exception):
    def __init__(self, msg):
        super().__init__(msg)


class ATECCInterface(Enum):
    SWI = 1
    I2C = 2


class ATECCRevision(Enum):
    ATECC508A = 0x5000
    ATECC608A = 0x6002
    ATECC608B = 0x6003

    @property
    def is_ATECC608(self) -> bool:
        return self in [ATECCRevision.ATECC608A, ATECCRevision.ATECC608B]

    @property
    def is_ATECC508(self) -> bool:
        return self in [ATECCRevision.ATECC508A]


class ATECCState(Enum):
    """ATECC state machine states
    When the device is asleep, it ignores all but the Wake condition.
    """

    IDLE = auto()
    SLEEP = auto()
    AWAKE = auto()


class ATECCErrorCode(int, Enum):
    SUCCESS = 0x00
    CHECKMAC_OR_VERIFY_MISCOMPARE = 0x01
    PARSE_ERROR = 0x03
    ECC_FAULT = 0x05
    SELF_TEST_ERROR = 0x07  # ATECC608A-TNGTLS
    HEALTH_TEST_ERROR = 0x08  # ATECC608A-TNGTLS
    EXECUTION_ERROR = 0x0F
    AFTER_WAKE = 0x11
    WATCHDOG_ABOUT_TO_EXPIRE = 0xEE  # ATECC608A-TNGTLS
    CRC_OR_OTHER_COMMUNICATION_ERROR = 0xFF  # ATECC608A-TNGTLS


class ATECCError(Exception):
    def __init__(self, code):
        super().__init__()
        self.code = code

    def __str__(self):
        try:
            return ATECCErrorCode(self.code).name
        except ValueError:
            return f"Unknown ATECC error 0x{self.code:02x}"


class ATECCOpCode(Enum):
    """ATECC command OpCodes"""

    CHECK_MAC = 0x28
    COUNTER = 0x24
    DERIVE_KEY = 0x1C
    ECDH = 0x43
    GEN_DIG = 0x15
    GEN_KEY = 0x40
    HMAC = 0x11
    INFO = 0x30
    LOCK = 0x17
    MAC = 0x08
    NONCE = 0x16
    PAUSE = 0x01
    PRIV_WRITE = 0x46
    RANDOM = 0x1B
    READ = 0x02
    SIGN = 0x41
    SHA = 0x47
    UPDATE_EXTRA = 0x20
    VERIFY = 0x45
    WRITE = 0x12
    AES = 0x51  # ATECC608A


class ATECCWordAddress(Enum):
    """Possible word-address for ATECC I2C writes."""

    RESET = 0x00
    SLEEP = 0x01
    IDLE = 0x02
    COMMAND = 0x03


class ATECCZone(Enum):
    """
    ATECC memory zones.

    Encoded values correspond to what must be transmitted in the READ commands.
    """

    CONFIG = 0
    OTP = 1
    DATA = 2


class SlotConfig:
    """ATECC data slot configuration."""

    def __init__(self):
        self.from_bytes(b"\x00\x00")

    def from_bytes(self, buf: bytes, offset=0) -> int:
        """
        Deserializes data from an input buffer.

        :param data: Input buffer.
        :type data: bytes
        :param offset: Offset of the data in the buffer.
        :type offset: int
        :return: Offset after the read data.
        :rtype: int
        """
        self.raw = buf[offset : offset + 2]
        x = int.from_bytes(self.raw, "little")
        self.write_config = (x >> 12) & 0x0F
        self.write_key = (x >> 8) & 0x0F
        self.is_secret = bool(x & (1 << 7))
        self.encrypt_read = bool(x & (1 << 6))
        self.limited_use = bool(x & (1 << 5))
        self.no_mac = bool(x & (1 << 4))
        self.read_key = x & 0x0F
        self.__check()
        return offset + 2

    def to_bytes(self) -> bytes:
        """
        :return: Data serialized to bytes.
        :rtype: bytes
        """
        self.__check()
        value = (
            (self.write_config << 12)
            + (self.write_key << 8)
            + (int(self.is_secret) << 7)
            + (int(self.encrypt_read) << 6)
            + (int(self.limited_use) << 5)
            + (int(self.no_mac) << 4)
            + self.read_key
        )
        return value.to_bytes(2, "little")

    def to_yaml(self) -> dict:
        """Generate dict object for yaml serialization"""
        self.__check()
        return {
            "write-config": self.write_config,
            "write-key": self.write_key,
            "is-secret": self.is_secret,
            "encrypt-read": self.encrypt_read,
            "limited-use": self.limited_use,
            "no-mac": self.no_mac,
            "read-key": self.read_key,
        }

    def from_yaml(self, data: dict):
        """Load attributes from yaml loaded dict"""
        self.write_config: int = data["write-config"]
        self.write_key: int = data["write-key"]
        self.is_secret: bool = data["is-secret"]
        self.encrypt_read: bool = data["encrypt-read"]
        self.limited_use: bool = data["limited-use"]
        self.no_mac: bool = data["no-mac"]
        self.read_key: int = data["read-key"]
        self.__check()

    def __check(self):
        """Check attributes types and values"""
        assert self.write_config in range(16)  # 4 bits
        assert self.write_key in range(16)  # 4 bits
        assert type(self.is_secret) is bool
        assert type(self.encrypt_read) is bool
        assert type(self.limited_use) is bool
        assert type(self.no_mac) is bool
        assert self.read_key in range(16)  # 4 bits


class ATECCInfoMode(int, Enum):
    REVISION = 0
    KEYVALID = 1
    STATE = 2
    GPIO = 3
    # The Persistent Latch Read mode of the INFO
    # command allows for reading the state of the persistent latch.
    # This is useful to verify the state of the persistent latch
    # when a key authorization has been connected to that latch.
    VOLATILE_KEY_PERMIT = 4


class Info:
    def __init__(self, mode: ATECCInfoMode, data: bytes, param=0):
        """
        Structure to hold information of the Info Command.

        :param mode: The mode of the Info command.
        :param data: The output payload
        :param param: Used for mode KEYVALID to indicate the Slot number.
        """
        self.mode = mode
        self.revision: Optional[ATECCRevision] = None
        self.raw = data
        self.param = param
        if data is not None:
            self.from_bytes(data)

    def from_bytes(self, data: bytes, offset: int = 0):
        """
        Deserialize data from an input buffer.

        :param data: Input buffer.
        :param offset: Offset of the data in the buffer.
        :return: Offset after the read data.
        """
        self.raw = data
        buf = bytes(data[offset : offset + 4])
        if self.mode == ATECCInfoMode.REVISION:
            self.revision = ATECCRevision(int.from_bytes(buf, "big"))
        if self.mode == ATECCInfoMode.STATE:
            self.tempkey_id = buf[0] & 0xF
            self.tempkey_sourceflag = bool((buf[0] >> 4) & 0x1)
            self.tempkey_gendigdata = bool((buf[0] >> 5) & 0x1)
            self.tempkey_genkeydata = bool((buf[0] >> 6) & 0x1)
            self.tempkey_nomacflag = bool((buf[0] >> 7) & 0x1)

            self.authvalid = bool((buf[1] >> 2) & 0x1)
            self.authkey = (buf[1] >> 3) & 0b1111
            self.tempkey_valid = bool((buf[1] >> 7) & 0x1)
        if self.mode == ATECCInfoMode.GPIO:
            # Successful return value if GPIO has been written to a 0 or 1
            self.gpio_written_value = buf[3]

    def __str__(self) -> str:
        ret = f"Info mode: {self.mode} : {self.raw.hex()}\n"
        if self.mode == ATECCInfoMode.REVISION:
            ret += f" revision: {self.revision}"
        elif self.mode == ATECCInfoMode.KEYVALID:
            zeros = b"\0" * 4
            ret += f" Key {self.param} is valid? {self.raw != zeros}"
        elif self.mode == ATECCInfoMode.STATE:
            ret += f" tempkey_id: {self.tempkey_id}\n"
            ret += f" tempkey_sourceflag: {self.tempkey_sourceflag}\n"
            ret += f" tempkey_gendigdata: {self.tempkey_gendigdata}\n"
            ret += f" tempkey_genkeydata: {self.tempkey_genkeydata}\n"
            ret += f" tempkey_nomacflag: {self.tempkey_nomacflag}\n"
            ret += f" authvalid: {self.authvalid}\n"
            ret += f" authkey: {self.authkey}\n"
            ret += f" tempkey_valid: {self.tempkey_valid}"
        elif self.mode == ATECCInfoMode.GPIO:
            if self.param == 2:
                ret += " GPIO value to write: 0\n"
            elif self.param == 3:
                ret += " GPIO value to write: 1\n"
            ret += f"GPIO written value: {self.gpio_written_value}"
        return ret
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

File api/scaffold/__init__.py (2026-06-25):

# This file is part of Scaffold
#
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
#
# Copyright 2019 Ledger SAS, written by Olivier Hériveaux


from enum import Enum, Flag, auto
from time import sleep
from typing import Any, Literal, Optional, Union
import serial.tools.list_ports
import serial.tools.list_ports_common
from packaging.version import parse as parse_version, Version as PackagingVersion
from .bus import ScaffoldBus, Register, TimeoutError

# Version of the Scaffold API
__version__ = "0.9.6b"

# Prevent flake8 from complaining about unused import. This class is actually
# re-exported. This should be improved in the future.
__all__ = ["TimeoutError"]


class Signal:
    """
    Base class for all connectable signals in Scaffold. Every :class:`Signal`
    instance has a Scaffold board parent instance which is used to electrically
    configure the hardware board when two :class:`Signal` are connected
    together.
    """

    def __init__(self, parent: "Scaffold", path: str):
        """
        :param parent: The :class:`Scaffold` instance which the signal belongs to.
        :param path: Signal path string. Uniquely identifies a Scaffold board
            internal signal. For instance '/dev/uart0/tx'.
        """
        self.__parent = parent
        self.__path = path

    @property
    def parent(self):
        """Parent :class:`Scaffold` board instance. Read-only."""
        return self.__parent

    @property
    def path(self):
        """Signal path. For instance '/dev/uart0/tx'. Read-only."""
        return self.__path

    @property
    def name(self) -> str:
        """
        Signal name (last element of the path). For instance 'tx'. Read-only.
        """
        return self.__path.split("/")[-1]

    def __str__(self) -> str:
        """:return: Signal path. For instance '/dev/uart0/tx'."""
        return self.__path

    def __lshift__(self, other: Union["Signal", Literal[0, 1]]):
        """
        Feed the current signal with another signal.

        :param other: Another :class:`Signal` instance. The other signal must
            belong to the same :class:`Scaffold` instance.
        """
        self.__parent.sig_connect(self, other)

    def __rshift__(self, other: "Signal"):
        """
        Feed another signal with current signal.

        :param other: Another :class:`Signal` instance. The other signal must
            belong to the same :class:`Scaffold` instance.
        """
        self.__parent.sig_connect(other, self)


class Module:
    """
    Class to facilitate signals and registers declaration.
    """

    def __init__(self, parent: "Scaffold", path: Optional[str] = None):
        """
        :param parent: The :class:`Scaffold` instance owning the module.
        :param path: Base path for the signals. For instance '/uart'.
        """
        self.__parent = parent
        self.__path = path
        self.__registers: list[Register] = []

    def add_signal(self, name: str) -> Signal:
        """
        Add a new signal to the object and set it as a new attribute of the
        instance.

        :name: Signal name.
        :type name: str
        :return: Created signal object
        :rtype: Signal
        """
        assert not hasattr(self, name)
        if self.__path is None:
            path = "/" + name
        else:
            path = self.__path + "/" + name
        sig = Signal(self.__parent, path)
        return sig

    def add_signals(self, *names: str) -> list[Signal]:
        """
        Add many signals to the object and set them as new attributes of the
        instance.

        :param names: Name of the signals.
        :type names: Iterable(str)
        :return: List of created signals
        :rtype: List(Signal)
        """
        return list(self.add_signal(name) for name in names)

    def add_register(self, *args: Any, **kwargs: Any) -> Register:
        """
        Create a new register.
        :param args: Arguments passed to Register.__init__.
        :param kwargs: Keyword arguments passed to Register.__init__.
        """
        reg = Register(self.__parent, *args, **kwargs)
        self.__registers.append(reg)
        return reg

    def __setattr__(self, key: str, value: Any):
        if key in self.__dict__:
            item = self.__dict__[key]
            if isinstance(item, Register):
                item.set(value)
                return
            else:
                super().__setattr__(key, value)
                return
        super().__setattr__(key, value)

    def reset_registers(self):
        """
        Call :meth:`Register.reset` on each defined register.
        """
        for reg in self.__registers:
            reg.reset()

    @property
    def parent(self) -> "Scaffold":
        """:class:`Scaffold` instance the module belongs to. Read-only."""
        return self.__parent
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

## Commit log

2019-03-29 Added hardware schematics, step and gerber files.
    [scaffold.gbl, scaffold.gbo, scaffold.gbp, scaffold.gbs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]
2019-04-04 API improvements.
    Added support for polarity option for pulses generators (was already
    supported by the hardware).
    Better board initialization to a default state: all signals are now
    disconnected at init. Pulse generators are reset to default
    configuration.
2019-04-05 Fixed issue with I/Os.
    Improved design to remove some glitches introduced by latest I/O
    features. Moved pin registration code from system.vhd to io_module.vhd.
2019-04-15 Added Altium project files.
    [Connectors.SchDoc, DUT_Platform.SchDoc, FPGA.SchDoc, LEDs.SchDoc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]
2019-04-24 Added daughter boards schematics and design.
    [breadboard.kicad_pcb, breadboard.sch, smartcard.kicad_pcb, smartcard.sch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]
2019-05-09 Added board status notice in readme.
2019-05-09 Added daughter-boards gerber files.
    [breadboard-B.Cu.gbr, breadboard-B.Mask.gbr, breadboard-B.Paste.gbr, breadboard-B.SilkS.gbr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]
2019-05-09 Renammed fab folders to gerber.
    [breadboard-B.Cu.gbr, breadboard-B.Mask.gbr, breadboard-B.Paste.gbr, breadboard-B.SilkS.gbr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]
2019-05-09 Added manufacturing files.
    Updated gerber and drill files (minor changes).
    Added BOM files.
    Added pick and place files.
    Added assembly and drill drawings.
    Updated Step model.
    [bom.xls, pp.csv, scaffold.gbl, scaffold.gbo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]
2019-05-22 Updated STM32 example script.
    Added options to load and execute code into RAM memory.
2019-05-27 Minor refactoring in API.
    Moved architecture base code of Scaffold class to a new class ArchBase.
    This will allow reusing code for other boards having the same design
    but not the same peripherals in the FPGA. The Scaffold class only
    declares the signals and peripherals specific to the Scaffold board.
2019-05-28 Removed debug print.
2019-07-16 New hardware version v1.1
    Reworked the adjustable regulators to fix stability issues and bad
    potentiometer routing.
    Replaced daughter-boards connectors with standard HE10 connectors and
    updated the pinout.
    Fixed glitching protection resistors value from 10 kOhm to 1 kOhm.
    Changed SMA connectors for better test points accessibility.
    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
    [Connectors.SchDoc, DUT_Platform.SchDoc, FPGA.SchDoc, LEDs.SchDoc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]
2019-07-16 Updated board status in readme.
2019-07-19 Added sockets v1.1 drawing in documentation.
2019-07-23 Updated daughterboards for the new Scaffold socket
    Update breadboard, smartcard and STM32F205 daughterboards to fit the
    new socket format of Scaffold v1.1 hardware.
    Previous socket format is now deprecated.
    [breadboard-B.Cu.gbr, breadboard-B.Mask.gbr, breadboard-B.Paste.gbr, breadboard-B.SilkS.gbr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]
2019-08-01 Added support for pull resistors.
    Updated VHDL code to drive pull resistors of Scaffold v1.1.
    Updated API to allow configuration of the pull resistors.
    Updated documentation.
    Architecture version is now 0.5.
2019-08-06 Added breadboard space to STM32F205 daughterboard.
    [stm32f205.kicad_pcb, stm32f205.sch]
2019-08-07 Fixed incorrect pin assignment for D3.
2019-08-07 Work on ISO7816 support.
    Enabling D0 programmable pull-up on Scaffold to avoid soldering it on
    smartcard daughterboards.
    Enabled card detection on smartcard daughterboards using the mecanical
    switch connected to D3.
2019-08-09 Added STM32F427 daughterboard.
    [stm32f427-B.Cu.gbr, stm32f427-B.Mask.gbr, stm32f427-B.Paste.gbr, stm32f427-B.SilkS.gbr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]
2019-08-12 Updated board tour picture.
2019-08-19 Fixed FPGA pin configuration.
2019-08-20 Enabled platform socket pins.
    Enabled platform socket pins in FPGA architecture.
    Updated Python API to use thoose new pins, namely p0 to p15.
2019-08-20 Added small utility to print board arch version.
2019-09-17 Updates in API.
    Better property names for the clock module.
    Added restart_dut, restart_platform and restart_all methods in power
    module.
2019-10-22 Fixed holes in breadboard daughterboard.
    Replaced plated holes with non-plated holes for easier solderability.
    [breadboard-B.Cu.gbr, breadboard-B.Mask.gbr, breadboard-B.Paste.gbr, breadboard-B.SilkS.gbr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]
2020-02-05 Added baudrate option in ArchBase class
    This allows setting the baudrate for other boards based on Scaffold
    architecture but with different serial speed.
2020-03-16 Automatic board detection
    Added script to configure Scaffold board USB description string (FTDI
    EEPROM programming).
    Added automatic detection of the board when no device is specified.
2021-01-06 Fixed board autodetection
2021-03-19 Added some commands to STM32 bootloader client
2021-07-21 Updated board animated picture
    Updated to the latest hardware board revision v1.1.
2021-07-21 Added serial number matching for board detection
    This new feature can be used to connect to the right board without
    worrying about serial device paths when multiple Scaffold boards are
    available.
2021-08-23 Minor update of ISO-7816 example
    Use board auto-detection instead of hardcoded serial device path.
2021-09-14 Added daughterboard base KiCad project files
    [base.kicad_pcb, base.kicad_sch]
2021-12-02 A0 to A3 board outputs now defaults to 0V
    When board is powered on or reset, A0 to A3 outputs now drive the
    signal to 0 instead of 3.3V or 5V.
2021-12-09 Fixes in timeout management
    Pushing a new timeout value cannot increase currently defined timeout.
2022-09-15 Added ATECC daughterboard design files
    [atecc-B.Cu.gbr, atecc-B.Mask.gbr, atecc-B.Paste.gbr, atecc-B.SilkS.gbr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]
2023-05-05 Added STM32 F100 (#13)
    STM32 F100 added
2023-10-10 Added STM32U59x/5Ax in known devices
2023-10-11 Added STM32U5A9ZJT6Q daughterboard
    [stm32u5a9zjt6q-B_Cu.gbr, stm32u5a9zjt6q-B_Mask.gbr, stm32u5a9zjt6q-B_Paste.gbr, stm32u5a9zjt6q-B_Silkscreen.gbr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]
2023-11-29 Added ESP32 daughterboard
    [esp32-B_Cu.gbr, esp32-B_Mask.gbr, esp32-B_Paste.gbr, esp32-B_Silkscreen.gbr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]
2023-11-29 Added ESP32 flash boot emulation script
2024-05-14 Added delays and buffer wait to the architecture
    Added two new operations to the Scaffold hardware architecture:
    - delay: wait for a given number of clock cycles
    - buffer wait: block execution until buffer has enough data
    Refactored commands management to increase performances: responses from
    the board are fetched as late as possible. This should make lazy
    sections obsoletes.
2024-05-14 Added FIFO buffer for transmission UART
    Added a FIFO buffer which stores the response bytes to be transmitted,
    which can improve board commands processing speed.
2024-05-14 Update STM32 script
2025-10-02 doc(daughterboards):Update Kicad daugtherboard/smartcard project and fix typo in schematics
    [smartcard.kicad_sch, smartcard.sch]

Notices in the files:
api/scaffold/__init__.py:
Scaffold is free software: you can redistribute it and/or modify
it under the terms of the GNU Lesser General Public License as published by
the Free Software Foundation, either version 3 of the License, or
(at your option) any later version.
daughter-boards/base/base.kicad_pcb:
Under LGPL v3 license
